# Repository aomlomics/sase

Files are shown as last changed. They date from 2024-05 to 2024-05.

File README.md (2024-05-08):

# sase

Subsurface Automated Sampler for eDNA (SASe)

Manuscript: Formel, N., Enochs, I. C., Sinigalliano, C., Anderson, S. R., & Thompson, L. R. (2021). Subsurface automated samplers for eDNA (SASe) for biological monitoring and research. HardwareX, 10, e00239. https://doi.org/10.1016/j.ohx.2021.e00239

Original code location (versions 1, 2, 3): https://data.mendeley.com/datasets/y3dgh36zt9/3

Files included (version 4):

File/folder name | File type | Open source license
-----------------|-----------|--------------------
SASeV4c.ino | Arduino code | CC BY 4.0
SASeBoard15 | Gerber Files | CC BY 4.0
SASe3DPrintFiles | 3Dprint Files | CC BY 4.0
SASeVectorFiles | Vector Files  | CC BY 4.0
BillofMaterials.docx | MS Word Doc | CC BY 4.0
BuildInstructions.pdf | PDF | CC BY 4.0
OperationInstructions.pdf | PDF | CC BY 4.0

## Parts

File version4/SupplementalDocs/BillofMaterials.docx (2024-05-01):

4. Bill of materials

Designator | Component | Number | Cost per unit (USD) | Total cost (USD) | Source of Materials | Material type
Fixed End Cap | Custom | 1 | $11.98* | $11.98 | 3D Printed on Form2 | Standard Black Resin
Flanged End Cap | Custom | 1 | $12.62* | $12.62 | 3D Printed on Form2 | Standard Black Resin
Acrylic Window | Custom | 1 | $0.50 | $0.50 | Laser Cut on BossLaser | Non-specific
Acrylic Test Cap | Custom | 1 | $0.50 | $0.50 | Laser Cut on BossLaser | Non-specific
End cap O-Ring | AS568-236 S70 Duro O-Ring | 1 | $0.56 | $0.56 | OringStore | Silicone
Lid | Custom | 1 | $11.43* | $11.43 | 3D Printed on Form2 | Standard Black Resin
Threaded inserts | Heat-sink threaded inserts (#4-40) | 4 | $0.19 | $0.77 | McMaster | Brass
Lid bolts | #6-32 x 1” Phillips Pan Head Machine Screws | 4 | $0.05 | $0.20 | AlbanyCountyFasteners | Stainless Steel
Lid nuts | #6-32 Nylon Insert Hex Lock Nuts | 4 | $0.04 | $0.16 | AlbanyCountyFasteners | Stainless Steel
PVC Pipe | 3” ID Schedule 40 PVC pipe, 4.25” long | 1 | $0.55 | $0.55 | HomeDepot | Non-specific
Motor Sleeve Left | Custom | 1 | $1.24* | $1.24 | 3D Printed on Form2 | Standard Black Resin
Motor Sleeve Right | Custom | 1 | $1.24* | $1.24 | 3D Printed on Form2 | Standard Black Resin
Motor Sleeve Screws | #4-40 x1/2” Phillips Pan Head Machine Screws | 8 | $0.03 | $0.24 | AlbanyCountyFasteners | Stainless Steel
Pumps | Peristaltic pumps-100 series 4mm Shaft; No Motor, 4 Rollers, 3mm Tubing Dia., Silicone Tubing | 2 | $9.92 | $19.84 | Williamson | Other
Pump Screws | #4-40 x 1” Phillips Pan Head Machine Screws | 4 | $0.05 | $0.20 | AlbanyCountyFasteners | Stainless Steel
Preservative Motor | 99:1 Metal Gearmotor 25Dx69L mm LP 12V with 48 CPR Encoder | 1 | $34.95 | $34.95 | Pololu | Other
Sample Motor | 34:1 Metal Gearmotor 25Dx69L mm LP 12V with 48 CPR Encoder | 1 | $34.95 | $34.95 | Pololu | Other
Motor shaft X-Rings | AS568-007 Buna-N 70 Durometer X-Rings | 2 | $0.07 | $0.14 | OringStore | Nitrile
Preservative Syringe | 10mL Luer Lock Dispensing Syringe | 1 | $0.82 | $0.82 | Grainger | Other
Filter | Sterivex™ filter 0.22um, luer lock (SVGVL10RC) | 1 | $10.79 | $10.79 | MilleporeSigma | Other
1/16” Tubing | 1/16” ID x 3/16” OD x 1/16” Wall Tubing, 2.75” long | 1 | $0.19 | $0.19 | USPlastics | Other
1/8 " Tubing | 1/8" ID x 1/4" OD x 1/16" Wall Tubing” 3" long | 1 | $0.23 | $0.23 | USPlastics | Other
Barbed Reducer | Straight Connector, 1/8" to 1/16" Barbed Reducer | 1 | $0.53 | $0.53 | Qosina | Other
Barbed Elbow | 1/8" Barb Elbow Connector | 1 | $0.50 | $0.50 | Qosina | Other
Barbed Tee | 1/8" Barb T Connector | 1 | $0.50 | $0.50 | Qosina | Other
Check Valve | Male-Female Luer Lock Check Valve, 2.9psi CP | 2 | $1.50 | $3.00 | Qosina | Other
Filter Barb | Male Luer Lock to 1/8" Barb Connector | 1 | $0.26 | $0.26 | Qosina | Other
Syringe Barb | Female Luer Lock to 1/16" Barb Connector | 1 | $0.21 | $0.21 | Qosina | Other
Straight connector | Straight Connector, 1/8" Barb | 1 | $0.00 | $0.00 | Williamson | Other
1/8" Clamp | Securing Clamp for 1/8" tubing | 8 | $0.25 | $1.97 | Qosina | Other
Sample Cartridge Cover | Custom | 1 | $6.51* | $6.51 | 3D Printed on Form2 | Standard Black Resin
Sample Cartridge | Custom | 1 | $7.11* | $7.11 | 3D Printed on Form2 | Standard Black Resin
Sample Cartridge Bolt | #6-32 x 1.25" Phillips Pan Head Machine Screws | 1 | $0.06 | $0.06 | AlbanyCountyFasteners | Stainless Steel
Sample Cartridge Wingnut | #6-32 Wingnut | 1 | $0.21 | $0.21 | AlbanyCountyFasteners | Stainless Steel
Housing Magnets | 1/8" Diameter x 1/16" Thick Magnet (D063CN52) | 8 | $0.56 | $4.48 | AmazingMagnets | Other
Circuit Housing | Custom | 1 | $4.26* | $4.26 | 3D Printed on Form2 | Standard Black Resin
Circuit Housing Faceplate | Custom | 1 | $4.53* | $4.53 | 3D Printed on Form2 | Standard Black Resin
Armature screws | #6-32 x 1.25" Flat Head Machine Screws | 2 | $0.05 | $0.10 | AlbanyCountyFasteners | Stainless Steel
Circuit Housing Screws | #4-40 3/4" Phillips Pan Head Machine Screws | 2 | $0.04 | $0.08 | AlbanyCountyFasteners | Stainless Steel
Circuit Board/Battery Cover Screw | #4-40 1/4" Phillips Pan Head Machine Screws | 3 | $0.03 | $0.09 | AlbanyCountyFasteners | Stainless Steel
IR Receiver | TSOP38238, 38.0kHz, 45m | 1 | $1.12 | $1.12 | Jameco | Other
OLED | 0.96 Inch Blue Yellow I2C OLED Display | 1 | $3.38 | $3.38 | AliExpress | Other
Reed Switch | 59050-010 | 1 | $1.18 | $1.18 | Digi-Key | Other
Microcontroller | Teensy 3.5 | 1 | $24.25 | $24.25 | PJRC | Other
microSD Card | 1gb microSD card, Class 4 | 1 | $4.95 | $4.95 | Sparkfun | Other
Coin Cell Holder | CR2032 Coin Cell Battery Holder | 1 | $0.07 | $0.07 | AliExpress | Other
Coin Cell | CR2032 Battery | 1 | $0.95 | $0.95 | Adafruit | Other
MOSFET | Power N-Channel MOSFET (IRLB8721) | 2 | $0.79 | $1.58 | Jameco | Other
Diode | 1N4004-TP Diode | 2 | $0.12 | $0.24 | Digi-Key | Other
1K Resistor | Resistor 1K 1/4W 1% AXIAL | 2 | $0.10 | $0.20 | Digi-Key | Other
390K Resistor | Resistor 390K 1/4W 1% AXIAL | 1 | $0.10 | $0.10 | Digi-Key | Other
100K Resistor | Resistor 100K 1/4W 1% AXIAL | 1 | $0.10 | $0.10 | Digi-Key | Other
3.3K Resistor | Resistor 3.3K 1/4W 5% AXIAL | 1 | $0.10 | $0.10 | Digi-Key | Other
Red Wire | 26 AWG Red Wire” 4" long | 1 | $0.05 | $0.05 | AllElectronics | Other
Battery Molex Connector | Molex 3 Position Connector Housing, 0022013037 | 1 | $0.19 | $0.19 | Digi-Key | Other
3-Pin Molex Connector | Molex 3 Position Connector Header, 0022232031 | 1 | $0.24 | $0.24 | Digi-Key | Other
Motor Molex Connector | Molex 6 Position Connector Housing, 0022013067 | 2 | $0.29 | $0.58 | Digi-Key | Other
6-Pin Molex Connector | Molex 6 Position Connector Header, 0022232061 | 2 | $0.43 | $0.86 | Digi-Key | Other
Crimp | Molex Connector 22-30AWG Crimp, 0008650816 | 15 | $0.29 | $4.35 | Digi-Key | Other
Circuit Board | Custom | 1 | $0.49 | $0.49 | SeeedStudio | FR-4
Battery Housing | Custom | 1 | $10.13* | $10.13 | 3D Printed on Form2 | Standard Black Resin
Battery Housing Cover | Custom | 1 | $1.66* | $1.66 | 3D Printed on Form2 | Standard Black Resin
Battery Cover Screws | #4-40 1/4" Phillips Pan Head Machine Screws | 2 | $0.03 | $0.06 | AlbanyCountyFasteners | Stainless Steel
Armature to Lid Screws | #6-32 1/4" Phillips Pan Head Machine Screws | 2 | $0.04 | $0.08 | AlbanyCountyFasteners | Stainless Steel
1/4” Heatshrink | 1/4" Heatshrink” 1" long | 1 | $0.02 | $0.02 | AllElectronics | Other
1/16" Heatshrink | 1/16" Heatshrink” 1" long | 1 | $0.01 | $0.01 | AllElectronics | Other
Header Pins | 24 Position Header Pin 2.54mm, 0022284240 | 1 | $0.82 | $0.82 | Digi-Key | Other
Batteries | AA Rechargeable NiMH | 8 | $4.17 | $33.35 | BatteryJunction | Other
IR Remote | Mini Remote Control, 21 Buttons, 38KHz NEC code output, 940nm IR LED | 1 | $4.95 | $4.95 | Adafruit | Other
Magnet | Any Standard Magnet | 1 | $0.75 | $0.75 | AmazingMagnets | Other
Preservative** | DNAGard (62001-046) 100mL | 1 | $240 | $240 | Biomatrica | Other
Solder | 24 AWG Lead-Free Wire Solder | 1 | $21.97 | $21.97 | Digi-Key | Other
Epoxy | E-90FL 2-Part Epoxy | 1 | $14.38 | $14.38 | Zoro | Other
Lubricant | Multi-Purpose Synthetic Grease | 1 | $4.69 | $4.69 | Walmart | Other

* The cost of 3D printed items was based on the cost of Formlabs standard black resin and the volume required

**The preservative identified here, DNAGard is no longer in production. However other preservatives can be substituted in the SASe that similarly allow ambient condition preservation of DNA such as Zymo Research DNA/RNA Shield (R1100-250)

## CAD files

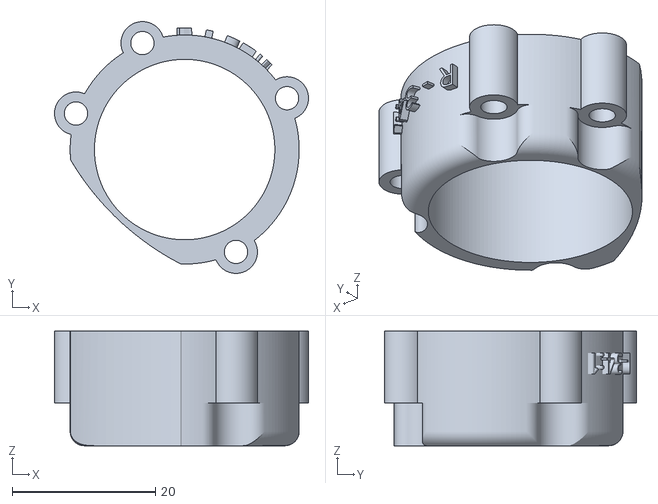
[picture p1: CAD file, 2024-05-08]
version4/DesignFiles/SASe3DPrintFiles/motorSleeveRight.stl
35.5 x 35.2 x 16.0

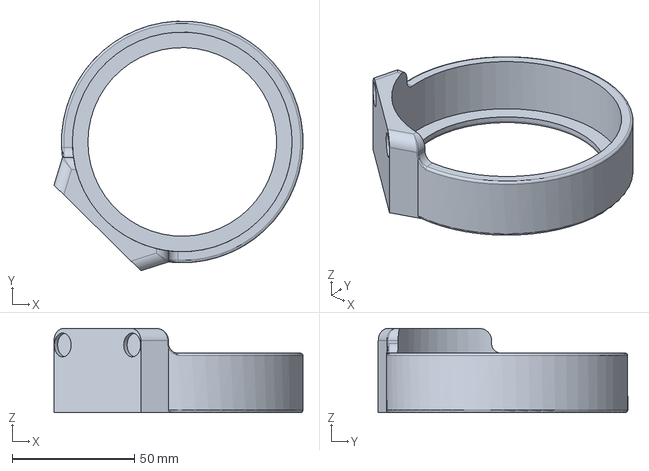
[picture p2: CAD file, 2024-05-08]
version4/DesignFiles/SASeStepFiles/SASe_fixedCap.step
102.0 x 102.2 x 34.5 mm

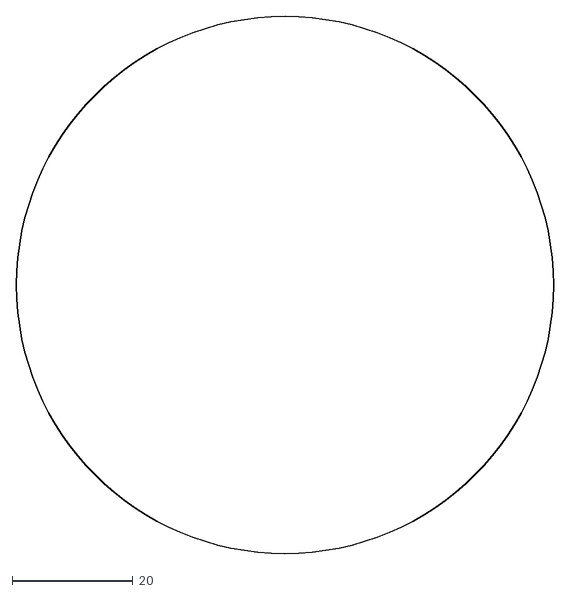
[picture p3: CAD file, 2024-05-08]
version4/DesignFiles/SASeVectorFiles/acrylicWindow.dxf
88.9 x 88.9

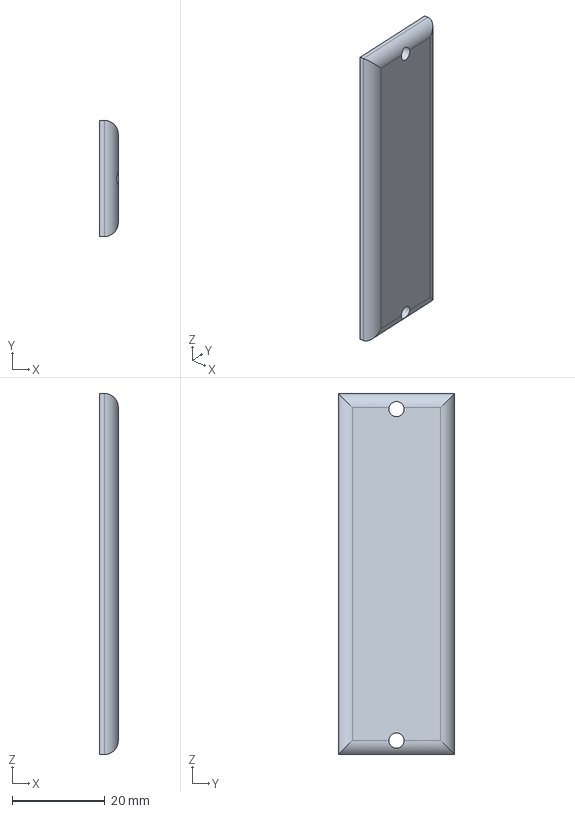
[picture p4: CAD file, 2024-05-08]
version4/DesignFiles/SASeStepFiles/SASe_battCover.step
4.00 x 25.0 x 77.7 mm

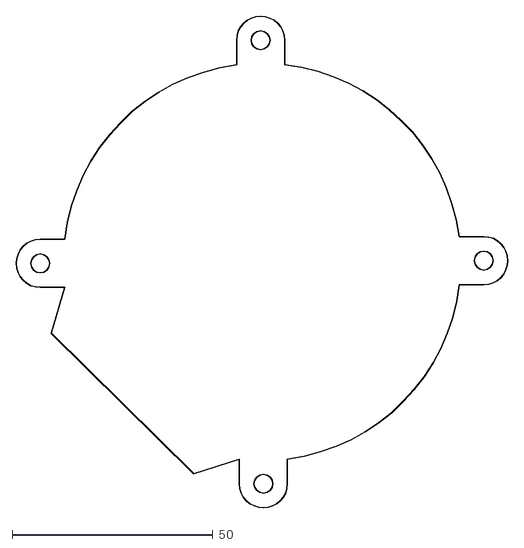
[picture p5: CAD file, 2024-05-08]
version4/DesignFiles/SASeVectorFiles/acrylicTestCap.dxf
122.5 x 122.5

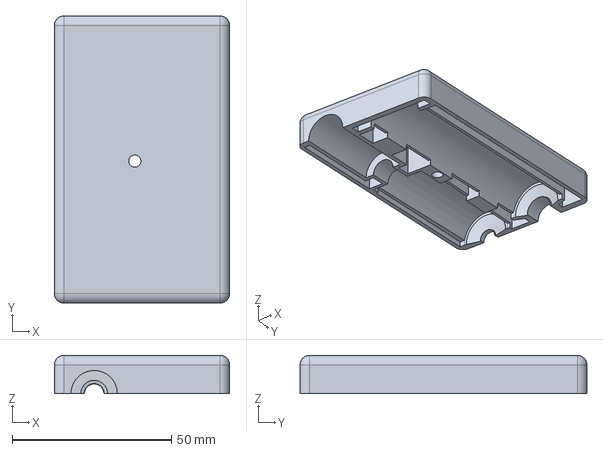
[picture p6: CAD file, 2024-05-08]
version4/DesignFiles/SASeStepFiles/SASe_topCover.step
55.0 x 90.0 x 12.0 mm

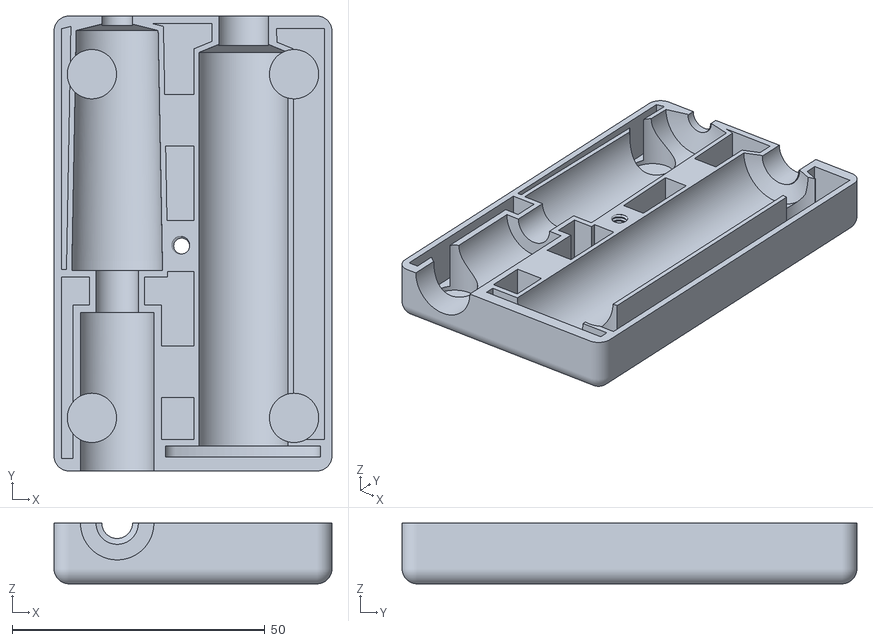
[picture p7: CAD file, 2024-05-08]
version4/DesignFiles/SASe3DPrintFiles/sampleCartridge.stl
55.0 x 90.0 x 12.0

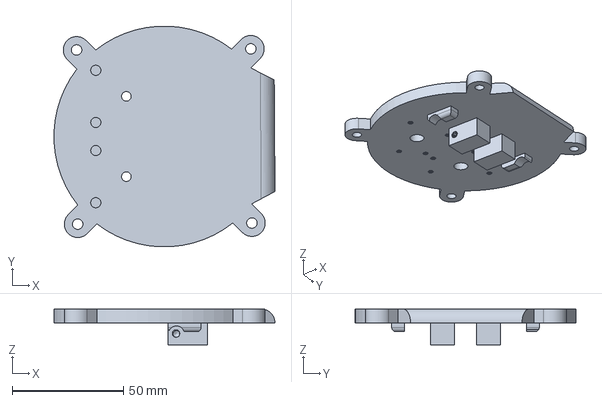
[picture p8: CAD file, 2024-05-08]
version4/DesignFiles/SASeStepFiles/SASe_motorMount.step
99.1 x 98.9 x 16.1 mm

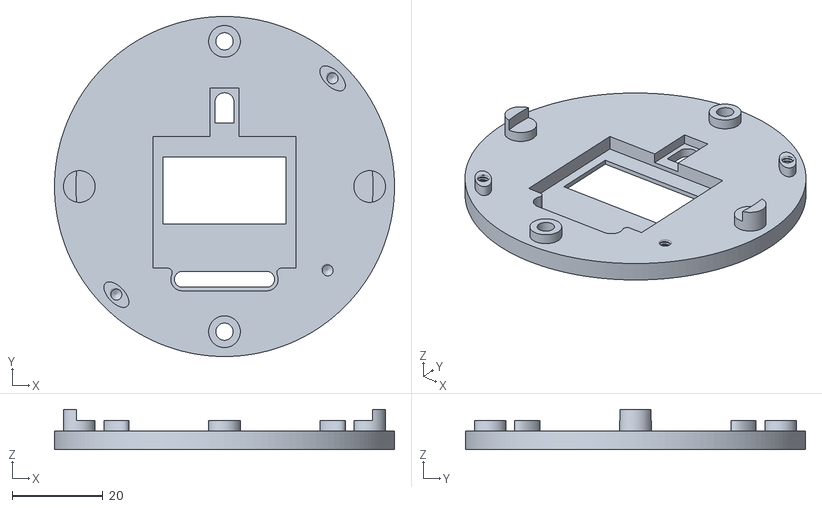
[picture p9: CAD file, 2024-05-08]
version4/DesignFiles/SASe3DPrintFiles/saseCHFacePlate.stl
74.9 x 74.9 x 8.93

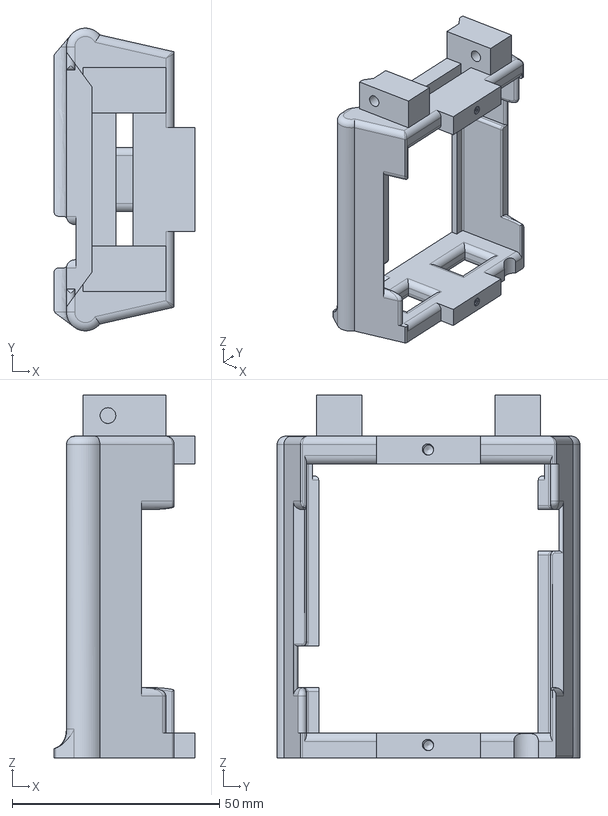
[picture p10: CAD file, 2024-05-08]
version4/DesignFiles/SASeStepFiles/SASe_battHolder.step
34.0 x 73.1 x 87.7 mm

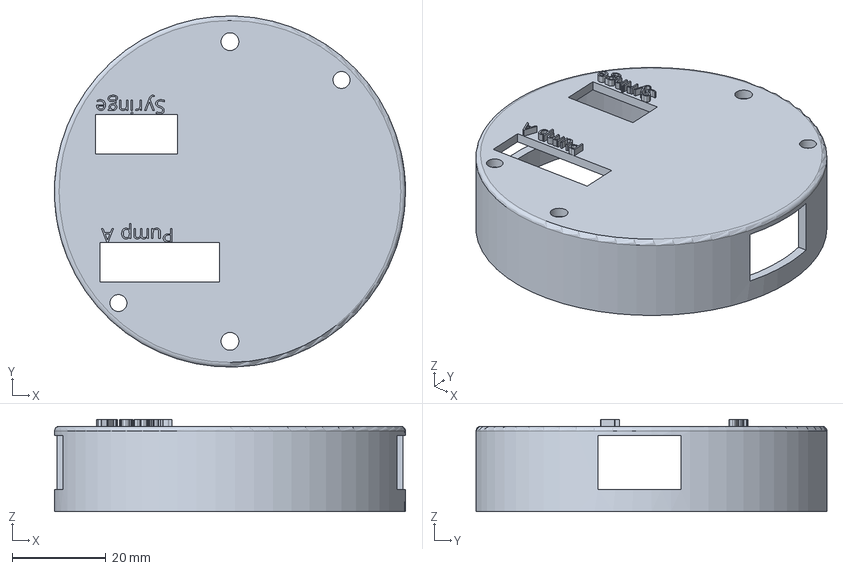
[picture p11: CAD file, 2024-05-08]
version4/DesignFiles/SASeStepFiles/SASe_circuitHousing.step
75.0 x 75.0 x 19.7 mm

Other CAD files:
version4/DesignFiles/SASe3DPrintFiles/saseFixedEndCap.stl
version4/DesignFiles/SASe3DPrintFiles/motorSleeveLeft.stl
version4/DesignFiles/SASe3DPrintFiles/sampleCartridgeCover.stl
version4/DesignFiles/SASeStepFiles/SASe_bottomCover.step
version4/DesignFiles/SASeStepFiles/SASe_facePlate.step
version4/DesignFiles/SASeStepFiles/SASe_motorSleeve2.step
version4/DesignFiles/SASeStepFiles/SASe_motorSleeve1.step
version4/DesignFiles/SASe3DPrintFiles/saseBattCover.stl
version4/DesignFiles/SASe3DPrintFiles/saseCircuitHousing.stl
version4/DesignFiles/SASeStepFiles/SASe_3inch_endcap.step

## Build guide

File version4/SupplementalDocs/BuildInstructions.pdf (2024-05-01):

### 5. Build instructions

All the 3D printed components in the design were made with SLA 3D printers. The SLA style

ensures the parts are waterproof, however, that need only applies to the three external parts

(fixed end cap, flanged end cap, and lid). The internal components could be made with a

different 3D printing style or other production method provided form was consistent with the

design. For 3D printing the default settings of the printer were used with a print resolution of

0.1mm and supports with rafting.

### 5.1. Housing construction

To prepare the components of the housing, sand the joining faces of the 3D printed end caps,

acrylic window, and the PVC pipe (Fig. 1) to improve adhesive bonding. Throughout the

construction process be sure to clean and dry areas prior to epoxying and remove excess epoxy to

avoid issues with fit and function. Apply a heavy bead of 2-part epoxy along the inside edge of

the flanged end cap (Fig. 2) and along the outside edge of one end of the PVC pipe. Push the

flanged end cap onto the PVC and give it a quarter twist to ensure even spread of the epoxy.

Place the joined parts with the end cap down and weight the PVC to improve stability during

curing of the epoxy, which should take 18-24 hours.

Apply a heavy bead of 2-part epoxy along the inside edge of the fixed end cap and press the

acrylic window into the end cap. Twist the acrylic window as needed to ensure even spread of

the epoxy and set the end cap with the acrylic facing up. Weight the acrylic to improve stability

during curing of the epoxy.

Once both parts are fully cured, add a heavy bead of 2-part epoxy along the inside wall of the

fixed end cap and the outside uncapped edge of the PVC pipe. Insert the PVC into the fixed end

cap and give the PVC a quarter twist to ensure even spread of the epoxy. At this point make sure

the magnet holes on the end caps are lying on the same plane and lined up. Failure to line up

these two surfaces will prevent the sampling cartridge from securely attaching. Once the fixed

cap is in place and lined-up set the housing down and weight the top piece to improve stability

during curing of the epoxy.

Once the housing is fully cured, insert the #6-32 x 1” bolts into the flanged end cap threaded

holes. Apply a small amount of lubricant to the end cap O-ring and place in the O-ring groove of

the flanged end cap. Install the acrylic test cap using the #6-32 lock nuts. Tighten the nuts down

until the O-ring is visually compressed. Throughout the construction process, be cautious

tightening screws on 3D printed parts to avoid overtightening and damaging the printed

components. Submerge the housing in water and watch for air bubbles escaping, which would

indicate a leak, and look for signs of water entry through the acrylic window. Minor leaks may

be fixed by identifying the location and adding more epoxy. This water test is not required but is

useful to prevent the discovery of leaks after the motors and electronics are installed, especially

on the first build.

### 5.2. Motor installation

Match the 34:1 motor with the 3D printed right motor sleeve, and the 99:1 motor with the left

sleeve and sand the contact faces of the top of the motors and the insides of the sleeves. Put a

heavy bead of 2-part epoxy around the top of the motor body and slide the motor sleeve onto the motor, twisting it around to improve the even spread of epoxy. Place the motor shaft-down with

the face of the motor and the face of the motor sleeve flush during curing. A board with holes for

the motor shaft can serve as a helpful jig for this step (Fig. 3). Failure to keep the motor and

sleeve face flush can impact the stability of the motor mount on the SASe lid.

To install the threaded #4-40 fittings into the SASe lid, first partially screw the fitting onto a #4-

40 screw. Apply a coat of 2-part epoxy to the outside of the fitting and then push the fitting into

position until the top is flush with the top of the lid (Fig. 3). Leave the fitting in place, carefully

remove the screw, and avoid pushing epoxy inside the fitting while the epoxy cures.

Once the motor sleeves are cured onto the motor, clip the length of the motor wires to 3.5 inches.

Run the wires for each motor through a 0.5-inch long piece of 1/4-inch heat shrink tubing. Install

a crimp onto the end of each wire and insert the crimped wires for each motor into a motor

Molex connector matching the original order (Fig. 4). Arrange the heat shrink tubing about

midway between the motor and the connector and apply heat to shrink for better wire

organization.

Apply a small amount of lubricant to the motor shaft X-rings and install them into the X-ring

seats on the inside of the SASe lid, using the shaft of the motor to push them into place. Once X-

rings are installed, push the shaft of the motors through the shaft holes in the lid. The 34:1 motor

used for sample collection and the 99:1 motor used for pumping preservative are positioned as

shown in Figure 5. Secure the motors in place with the #4-40 x ½ inch screws through the motor

sleeves. The screws will fit flush with the motor sleeves and should not be more than “finger

tight”.

Once the threaded fittings have cured in the lid, install the two peristaltic pumps onto the motor

shafts, oriented so the pump mounting holes line up with the fittings. Secure the pumps in place

using the #4-40 x 1-inch screws. Install the 1/8-inch barbed connector into the left tube of the

sample pump head (Fig. 6). Cut the 1/8-inch tubing into a 2.25-inch long piece and a 3/4-inch

long piece. Install the 1/8-inch barb tee connector on one end of the 2.25-inch long section and

the 1/8-inch male luer lock fitting on the other end. Attach the 3/4-inch section of tubing to the

free end of the tee. On the other end of the tubing attach the 1/8-inch elbow connector. Slide a

1/8-inch tube clamp onto the inside tube of each pump and then install the fitting/tubing combo

into the two pump heads as pictured in Figure 6. Once inserted, tighten clamps to secure the

fittings. Insert the 1/8-inch to 1/16-inch reducer fitting into one end of the 2.75-inch long 1/16-

inch tubing. On the free end of the 1/16-inch tubing, insert the 1/16-inch barb to female luer lock

fitting. Insert the 1/8-inch barb into the free tube of the preservative pump to complete the SASe

plumbing.

At this point, the housing can be water-tested again to ensure the X-rings were installed properly.

Install the lid with mounted motors and pumps and secure with the #6-32 lock nuts. Submerge

the housing in freshwater and ensure there are no leaks.

### 5.3. Power source construction

The battery pack holds eight AA batteries and has ground and 12-volt wire connections. To add a

6-volt power source, install the 4-inch red wire into the battery pack midway between the 12-volt

wire and the ground wire (Fig. 7). To install the wire, strip 1/8-inch of the insulation off one end

of the wire and 1/4-inch of the insulation off the other end. Put the 1/4-inch side of the wire

through the negative terminal indicated in Figure 7 and wrap the uninsulated wire around the

terminal to make a more stable connection, then solder the wire in place. Clip the original wires

to match the length of the new 6V wire, using the connection of the 6V wire as the starting point

for measurement, and strip off an 1/8-inch of insulation from the ends. Put a 1-inch long piece of

1/16-inch heat shrink around the wires to keep them together and install a crimp on the end of

each of the three wires. Install the wires into the battery Molex connector (Fig. 7).

Attach the 3D-printed battery housing to the lid using the two #6-32 x 3/4-inch long armature to

lid screws. With the battery pack updated, install eight AA batteries and insert the battery pack

into the 3D-printed battery housing. Secure the battery pack in place with the 3D-printed cover

and the two #4-40 x 1/4-inch long screws.

### 5.4. Circuit board construction

The circuit board can be milled in-house, but the quality and cost of ordering printed circuit

boards (PCB) make that the better option. This project had circuit boards milled by Seeed Studio

(seeedstudio.com/fusion.html) using the circuit board design files (SASeBoard15.zip) and the

following parameters:

PCB Dimension: 64.2mm*64.2mm

Impedance Control: No

Surface Finish: HASL

Min Solder Mask Dam: 0.4mm↑

Copper Weight: 1oz.

Half-cut / Castellated Holes: No

Min Hole Size: 0.3mm

PCB Color: Blue

Material: FR4 TG130

Layer: 2

Blind Vias: No

PCB Thickness: 1.6mm

Min Tracking / Spacing: 6/6mil

Plated Half-holes / Castellated Holes: No

Installation of the circuit board components is described here in order of installation. Solder the

headers, resistor, and diodes in place on the PCB (Fig. 8). The direction of the resistors is not

important but take care to orient the diodes as pictured on Figure 8 to ensure proper current flow.

Clip the excess pins from the bottom of the board. Install the 3-pin and two 6-pin Molex

connectors and solder the pins on the bottom of the board. Install the MOSFETs with enough

clearance to be bent at an angle above, but not touching, the diodes. Solder the MOSFETs in

place and clip the excess pins from the bottom of the board. Solder the 4-pin header onto the

OLED, and then flip the PCB over and install and solder the OLED in place on the bottom of the

board (Fig. 9). Bend the IR receiver pins at a right angle to the receiver and install and solder the

receiver with about 2 mm of space between the back of the receiver and the board. Install the reed switch in place and solder the pins. Clip any excess pins on the top of the board. Install the

RTC coin cell battery holder into the top of the board (Fig. 10). To solder the battery holder pins

the IR receiver on the bottom of the board needs to be bent gently upwards. Once the pins are

soldered and clipped, gently bend the receiver back into a horizontal position. Lastly, install the

Teensy on the headers and solder in place.

### 5.5. Preparation of the microSD card and software programming

Using a text editor program, create the two text files for recording sample logs (dataLog.TXT)

and storing settings and sample parameters (sampleParam.TXT). The dataLog file is a blank file

for logging sample times and requires no text. The sampleParam file requires a line of text with

nine integers.

Example: 1,1000,10,-1000,11,30,18,11,19

Key: Sample Mode (0 = Daily, 1= Once), Sample Volume (mL), Calibration Volume (mL),

Calibration Count, Sample Time (Hr), Sample Time (Min), Sample Day, Sample Month, Sample

Year

Input an appropriate line of text for the sampleParam file, save both text files on the microSD

card, and insert the card into the Teensy.

To upload the operating code to the SASe requires the Arduino software (IDE) and the

Teensyduino add-on. Once installed, place the SASe code (SASeV3c.ino) in a folder labeled

identically (i.e., SASeV3c) within the Arduino library folder. Run the Arduino program and use

the Library Manager to search for and install the most recent versions of:

- Adafruit GFX Library by Adafruit

- Adafruit SSD1306 by Adafruit

Also, because more recent versions have not been made compatible at this time, install version

1.1.4 of:

- SdFat by Bill Greiman

To set the OLED display resolution navigate to the Adafruit_SSD1306 folder (…\Arduino\

libraries\). Open the Adafruit_SSD1306.h file with a text editor and scroll down to the following

line:

// | #define SSD1306_128_64
| #define SSD1306_128_32
// | #define SSD1306_96_16

The default setting is the 128 x 32 bit screen resolution but the SASe OLED resolution is 128 x

64 bit. To fix this, uncomment the 128 x 64 bit screen resolution by deleting the two forward

slashes in front of SSD1306_128_64 and add two forward slashes in front of SSD1306_128_32:

#define SSD1306_128_64

// | #define SSD1306_128_32
// | #define SSD1306_96_16

Save and close the text file. To maximize sleep time for the Teensy and the SASe, the low

current draw Snooze library needs to be edited. Navigate to the Snooze src folder

(…\Arduino\hardware\teensy\avr\libraries\Snooze\) and use a text editor to edit and save these two files: SnoozeAlarm.h and SnoozeAlarm.cpp. In SnoozeAlarm.h find the line near the bottom

of the document that reads:

void setRtcTimer( uint8_t hours, uint8_t minutes, uint8_t seconds );

Change that line to:

void setRtcTimer( uint32_t hours, uint32_t minutes, uint32_t seconds );

In SnoozeAlarm.cpp, find the line near the top of the document that reads:

void SnoozeAlarm::setRtcTimer( uint8_t hours, uint8_t minutes, uint8_t seconds ) {

Change that line to:

void SnoozeAlarm::setRtcTimer( uint32_t hours, uint32_t minutes, uint32_t seconds ) {

Save and close both text files. The SASe code is ready to be uploaded onto the Teensy

microcontroller. Use the Arduino program to open the SASe code. Under the Tools menu select

“Board:” and choose Teensy 3.5. Connect the Teensy microcontroller to the computer with a

micro USB to USB cord. Under the Tools menu select “Port:” and choose the serial port

connected to the Teensy. Select the Upload arrow in the top left corner to verify and compile the

code onto the Teensy. Verify the upload worked by looking at the OLED on the circuit board. If

it worked, the screen will display the Status Menu. Once the code is uploaded and the OLED is

displaying properly, disconnect the Teensy and install the circuit board into the 3D printed

faceplate using one #4-40 x 1/4-inch screw (Fig. 10). Install the 3D printed circuit housing on the

faceplate, being sure to line up the Molex connectors with the openings in the housing (Fig.

11A). Attach the circuit housing to the faceplate using two #4-40 x 3/4-inch screws. Attach the

completed circuit housing to the armature using two #6-32 x 1.25-inch screws (Fig. 11B).

### 5.6. Sampling cartridge construction

To install the magnets for the sampling cartridge and end caps it is important to keep track of the

polarity of the magnets so that they are all installed in the same direction. Put a dot of two-part

epoxy into each of the magnet spaces on the bottom of the sampling cartridge and then press the

magnets into place until fully seated (Fig. 12). The magnets in the end caps of the SASe must

also be installed with the polarity in the same direction as the sampling cartridge magnets. Place

a dot of two-part epoxy in the magnet spaces on each of the end caps and press the magnets into

position. Allow all epoxied magnets to cure before testing. Once cured, attach the cover of the

sample cartridge using the #6-32 x 1.25-inch bolt and the #6-32 wingnut, then attach the

sampling cartridge to the SASe housing via the magnets.

### 5.7. Final preparation

With all components now complete, connect the two pump motors and the power connection to

the circuit board. The circuit housing is labeled to identify where each motor attaches. Connect

the preservative motor to the 6-pin Molex connector labeled “Syringe”, connect the sample

motor to the 6-pin Molex connector labeled “Pump A”, and connect the battery to the 3-pin

Molex connector inside of the sample motor connection (Fig. 13). Route the wires so they are not

touching the motor rotary encoders to avoid wear on the wires when the motors are running. If

properly assembled, the SASe OLED will turn on and display the Status Menu. Slide the internal

components of the SASe into the waterproof housing and secure the lid with the four lock nuts.

Figures:

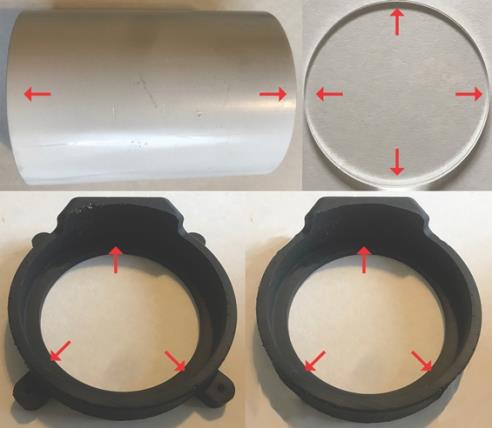
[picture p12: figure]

Figure 1: Red arrows indicate the surfaces to sand and clean in preparation for epoxying.

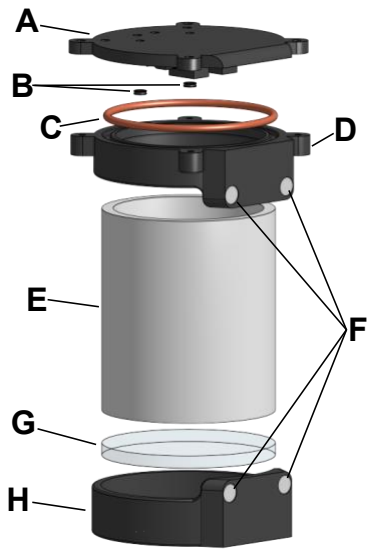
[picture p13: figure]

Figure 2: The SASe housing is made up of a 3D-printed lid (A), two X-rings for the motor shafts

(B), O-ring for the lid seat (C), 3D-printed flanged end cap (D), 3” PVC body (E), four sample

cartridge connection magnets (F), ¼” acrylic window (G), and a 3D-printed fixed end cap (H).

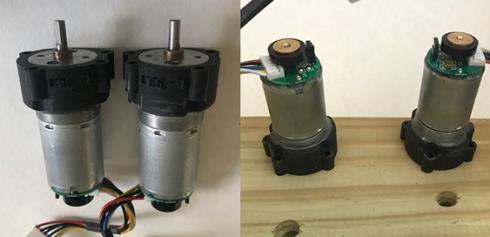
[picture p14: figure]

Figure 3: The motor sleeves and the face of the motor need to be flush. Using a jig can help hold

that position while the epoxy is curing.

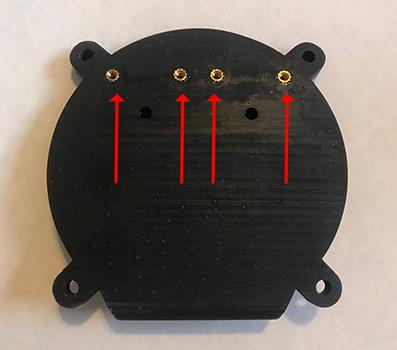
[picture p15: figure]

Figure 4: Threaded fittings are installed on the outside face of the 3D printed lid.

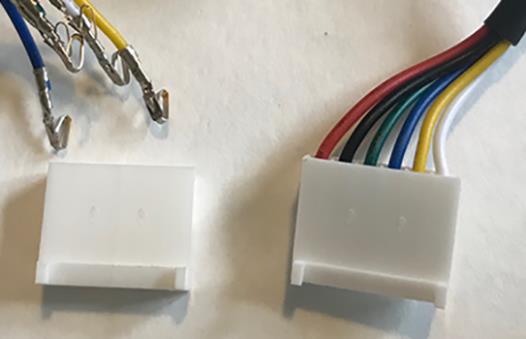
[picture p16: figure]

Figure 5: The crimped wires are inserted in the motor connectors in the order shown on the right.

Wire ID: Red (Power), Black (Power), Green (Ground), Blue (VCC), Yellow (Encoder A

output), White (Encoder B output).

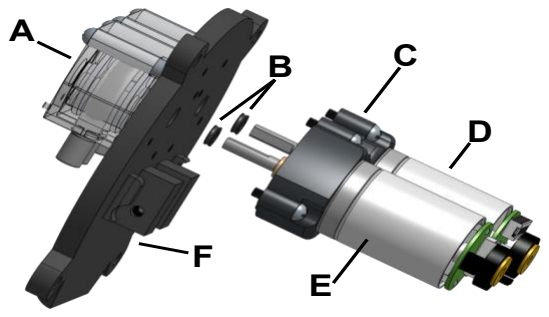
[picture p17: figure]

Figure 6: The two peristaltic pumps (A) are mounted to the outside of the 3D-printed lid (F). The

34:1 (D) and the 99:1 (E) DC motors are epoxied to 3D-printed motor sleeves (C) mounted on

the inside of the lid. The motor shafts insert into the peristaltic pumps through the lid and an X-

ring on the shaft of each of the motors (B) keeps the shaft-lid interface watertight.

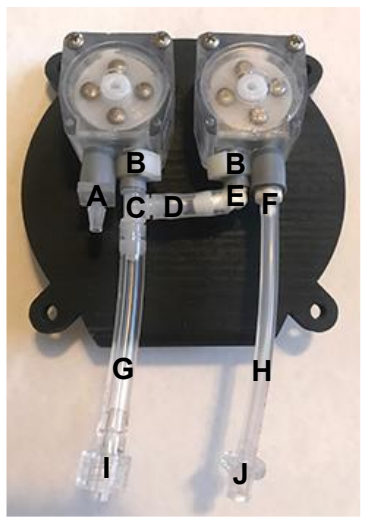
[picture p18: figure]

Figure 7: The pump heads are secured on the outside of the SASe lid, and the plumbing

components for transporting sample water and preservative are installed as pictured and include

the 1/8-inch barbed connector (A), 1/8-inch tube clamps (B), 1/8-inch barb tee connector (C),

0.75-inch long 1/8 ” tubing (D), 1/8-inch elbow connector (E), 1/8-inch to 1/16-inch reducer

fitting (F), 2.25-inch long 1/8-inch tubing (G), 2.75-inch long 1/16-inch tubing (H), 1/8-inch

male luer lock (I), 1/16-inch barb to female luer lock fitting (J).

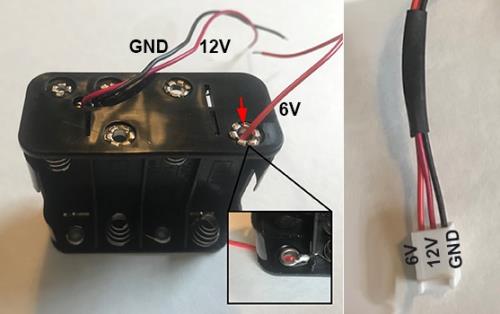
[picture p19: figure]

Figure 8: Solder a 6V wire to the OEM battery pack at the terminal indicated by the red arrow.

The inset shows the wire looped around the inside of the terminal to add stability to the

connection. Install the crimped wires into the Molex connector as pictured.

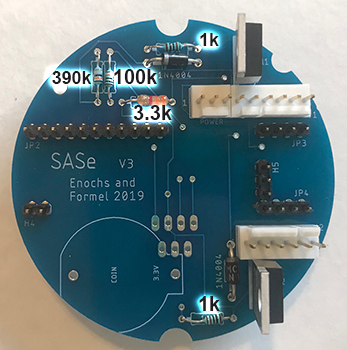
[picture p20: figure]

Figure 9: The headers, resistors, diodes, MOSFETs, and Molex connectors are installed as

pictured.

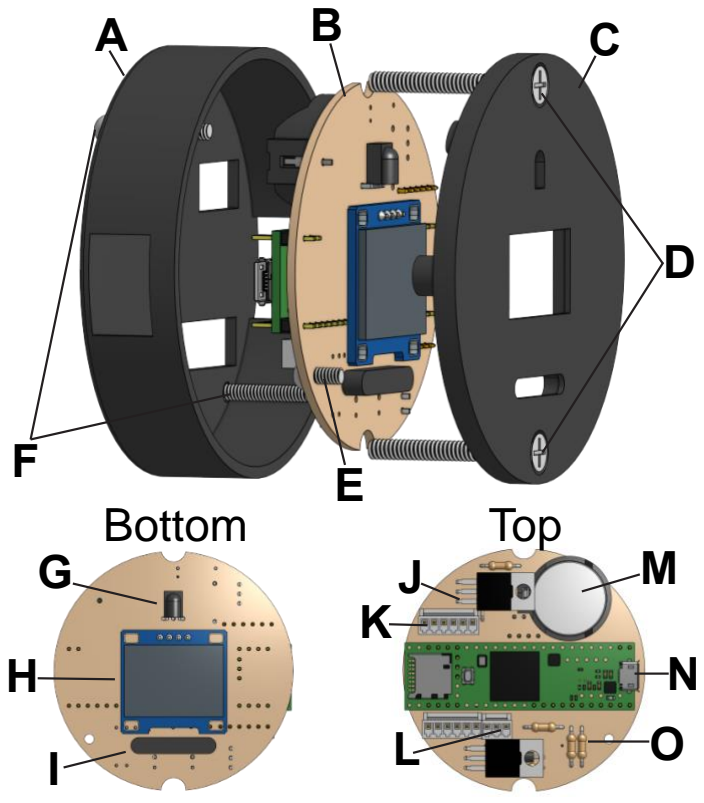
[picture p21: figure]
Bottom; Top

Figure 10: The 3D-printed circuit board housing (A) holds the SASe circuit board (B) and the UI

components are visible through the 3D-printed faceplate (C). The whole housing is mounted on

the main armature with two #6-32 bolts (D), while one #4-40 bolt (E) secures the circuit board to

the faceplate, and two #4-40 bolts (F) hold the housing together. The circuit board is labeled to

show the top and bottom and all PCB components are labeled as follows: IR receiver (G), OLED

(H), reed switch (I), N-channel MOSFET (J), Molex 6-pin connector (K), Molex 3 pin connector

(L), coin cell battery (M), Teensy 3.5 (N), resistors (O). Not visible are the two diodes below the

MOSFETs that control current flow for the motor circuits.

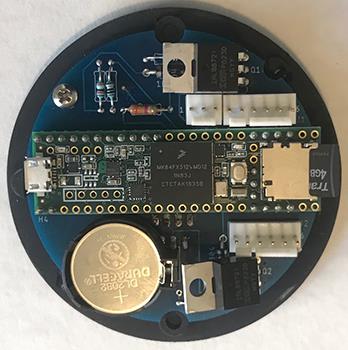
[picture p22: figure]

Figure 11: Install the coin cell holder and solder the pins on the bottom of the board then install

the Teensy microcontroller and solder the pins. The finished circuit board is installed onto the 3D

printed faceplate.

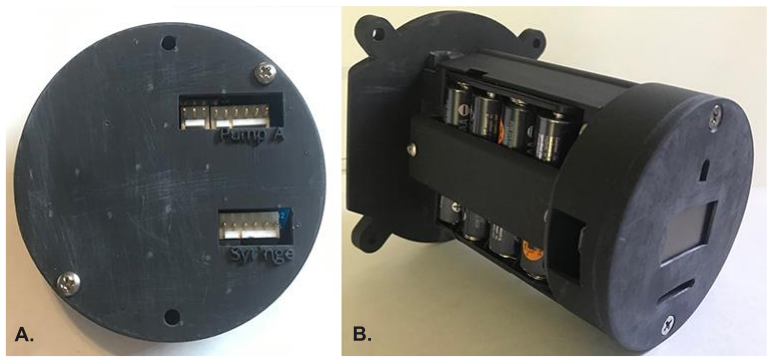
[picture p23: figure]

Figure 12: The 3D printed circuit housing (A) with openings for Molex connectors is attached to

the armature (B) to connect the internal components of the SASe.

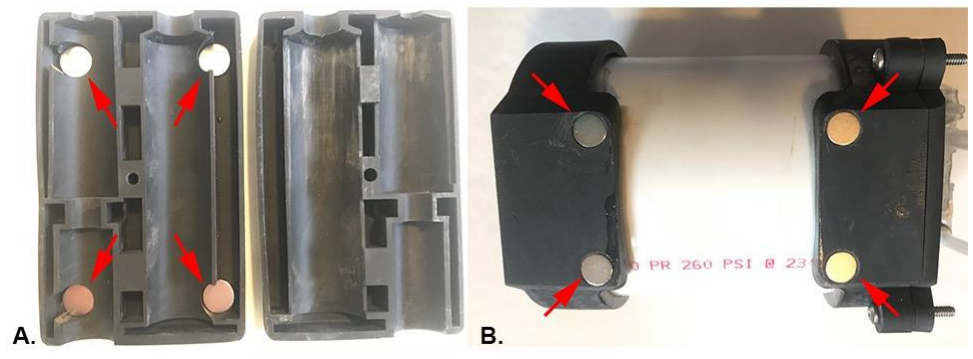
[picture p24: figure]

Figure 13: The sample cartridge (A) and the end caps (B) both require magnets installed as

indicated by the red arrows.

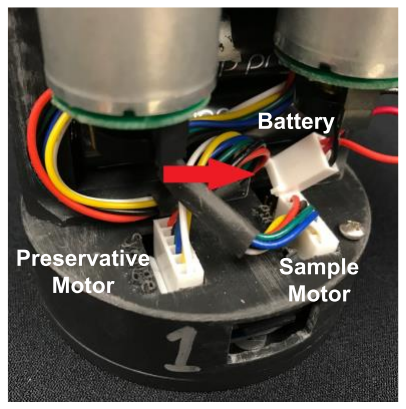
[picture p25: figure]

Figure 14: The connections for the SASe motors and battery are labeled, and the battery

connection location is indicated by the red arrow.

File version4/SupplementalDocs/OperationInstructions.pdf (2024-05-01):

### 6. Operation instructions

### 6.1. User interface

Once the batteries are attached to the SASe circuit board the OLED screen will turn on and

display the Status Menu (Fig. 1). To navigate through and within the SASe menu screens, use the

four cursor keys and the enter button of the IR remote, the left and right cursors will navigate

between menus from the top of the screen (Fig. 2). Settings are saved by selecting “ENTER

SET” and pressing enter.

### 6.2. Calibration

The peristaltic pumps have an advertised pump rate of 0.2mL per revolution, but there is

variability by pump head, so a calibration step uses the motor’s rotary encoder and user input to

measure the actual pump rate and improve accuracy of sampling volume. To run the calibration,

install a fresh Sterivex filter onto the filter luer lock connection, including the one-way check

valves on either end of the filter (Fig. 3). Connect a piece of 1/8-inch tubing to the inflow

connection of the sampling pump and put the other end of the tubing into a water cup. Direct the

outflow of the filter into a graduated cylinder. With the Status Menu on the screen press the left

cursor on the IR remote to navigate to the Prime Menu. Use the down cursor on the IR remote to

navigate the cursor to the row labeled “RUN WATER”, then hit enter on the remote. The

sampling pump will turn on and can be turned off by pressing enter on the remote again. The

tubing and filter should be fully primed with water before starting the calibration to ensure

accurate results. Position the outflow of the filter to flow into an empty graduated cylinder. Use

the left cursor to navigate to the Calib Menu. Select “RUN CAL” and press the enter key on the

IR remote. The sampling pump will turn on for 30 seconds. Measure the amount of water transferred to the graduated cylinder when the pump stops. Use the IR remote and the up and

down cursors to enter the volume of water collected on the “VOL:” line. Select ENTER SET and

press enter to save the calibration. The screen will display <SAVED> to show it was saved.

After calibration, the sampling pump has an accuracy of ±5% of the target volume (Fig. 4).

### 6.3. Set time

Once the calibration is set, the RTC on the microcontroller should be set. Navigate to the Time

menu. The first row is the time in HH:MM:SS and the second row is the date in DD/MM/YY.

Change the numbers using the up and down cursors to match up with the time and date. Select

and press enter on “ENTER SET” to synchronize the RTC with set time. The correct time will

now be displayed in the Status Menu.

### 6.4. Set sample mode, collection time, and date

The sampler can operate in two different modes: Once and Daily. Once mode will sample a set

volume at a single given time and date and then wait in sleep mode until woken up and

reprogrammed. Daily mode will sample a set volume at a given time every day starting on the

date selected. Navigate to the Settings Menu and select “Mode”; use the up and down cursor to

switch between “Once” and “Daily”. The next line allows the sample volume to be adjusted. The

up and down cursors can be used to increase or decrease the volume in increments of 10 mL with

an upper limit of 2000 mL. Once the mode and volume have been chosen, select “ENTER SET”

and press enter to save the settings.

Navigate to the Pump Menu. The first line (T) is the time setting for an alarm to go off and activate the sampling programming while the second line (D) is the date. Both options will

always be available, but the date will only be displayed on the Status Menu for Once Mode.

Daily mode uses the pump date to determine when daily sampling begins, but on the Status

Menu only the time of sampling will be displayed. Use the up and down cursors to adjust the

time (HH:MM) and date (DD/MM/YY) and then select “ENTER SET” and press enter to save

the pump alarm time. Navigate to the Status Menu to review the input settings and confirm the

current time.

### 6.5. Initiate sampling mode

After calibrating the sampler and inputting the settings the pump needs to be in a sleep mode to

save battery life and initiate sampling tasks. Navigate to the Initiate Menu. Select “Press Enter”

and press enter on the IR remote. The sampler will go into sleep mode. The time, date, and

battery voltage will be logged on the dataLog.txt file on the microSD card when sampling starts.

If the SASe is set to go off within 60 seconds of sleep mode being initiated “Wait...” will be

displayed on the screen until the sampling starts. When the sampling mode begins, the sampling

pump is activated and the screen will read “SAMPLING”. At this point the pump will run until

the programmed volume of water has been filtered and the program cannot be interrupted with

the reed switch. Once the sample has been taken, the sampling pump will turn off and the

preservative pump will turn on. The screen will read “SYRINGE” and the preservative pump

will run until five mL of preservative has been pumped into the filter housing. If the SASe is set

to Once mode it will return to sleep mode and stay that way until woken up with the reed switch

or until the batteries die. If it is in Daily mode it will add 24 hours to the sample time and date and start sleep mode again, until the sampler is woken up with the reed switch or until the

batteries die.

### 6.6. Interrupt sampling mode

While the SASe is in sleep mode, no changes can be made to the settings. To wake the sampler

up from sleep mode and allow changes to be made, the reed switch on the face of the sampler

must be activated. To activate the reed switch, press a magnet against the acrylic faceplate and

move it back and forth in front of the black reed switch (Fig. 2). After 2-3 seconds, the sampler

will come out of sleep mode and display “REED!” on the OLED before displaying the Status

Menu.

### 6.7. Deployment

Before deploying the SASe the O-ring should be lubricated, fully charged batteries installed, and

all securing screws and nuts carefully tightened to ensure a waterproof seal. Take care when

lubricating the O-ring to ensure it is clean of dirt, hair, or other debris that could break the

waterproof seal. Install a new Sterivex filter capped by check valves into the sampling cartridge

and fill the preservative syringe. Secure the cover of the sampling cartridge using the #6-32 bolt

and wingnut. Attach the filter connection and the syringe connection to the filter inflow check

valve and the syringe, respectively (Fig. 3). Attach the filter cartridge to the SASe housing via

the magnets.

To prevent an airlock in the tubing or compression of the filter air space when the SASe is

deployed at depth, prime the filter with molecular-grade water prior to deployment. Use a clean syringe to fill the filter or place the inflow of the sampling pump into the water source and use

the Prime Menu’s “RUN WATER” command.

The SASe is slightly negatively buoyant but it should be attached to a dive weight or to an

underwater structure to prevent it from moving in waves or current. If attached to a solid

structure, the SASe should be tightly secured to prevent wear on the housing. For long

deployments, large stainless-steel hose clamps work better than zip ties which can stretch and

loosen under stress over time.

Once a sample has been collected, the filter or the entire sampling cartridge must be replaced to

continue daily sampling or set new dates and time for single sampling. New filters must have

check valves and be primed with purified water. This filter/cartridge replacement can be done as

many times as the battery life will allow, typically five to six times for 1000mL samples.

Completed samples are returned to the lab for analysis. The preservative acts to preserve the

DNA samples for weeks to months at room temperature [1, 2]. The check valves on the filter

have a 2.9 psi cracking pressure to prevent sample contamination, loss, or dilution; however, the

filters should be further sealed with luer lock caps after collection to ensure no sample is lost due

to rough handling while awaiting laboratory analysis.

### 6.9. Downloading sample data

To retrieve sampling data, remove the internal armature from the housing and remove the

microSD from the circuit housing. Download the two text files, sampleParam.txt and

dataLog.txt. The sampleParam file retains the settings and sampling parameters as described earlier. The dataLog file has a line of text for every sample taken which includes the sampling

start time and battery voltage.

Example: 9:30:1,18/11/2019,10.74

Key: Hr:Min:Sec (Sampling started),Day/Month/Year (Sampling started),Voltage (volts)

The programming for the SASe requires these two text files to operate; do not remove the files

from the microSD card when downloading the data and reinstall the card before storing or

redeploying the SASe.

### 6.9. Cleaning

The SASe should be rinsed and cleaned with freshwater to remove any sediment, growth, and/or

salt. The tubing for the sample and preservative pumps should be rinsed with molecular-grade

water using the Prime Menu’s “RUN WATER” and “RUN SYR.” command. Press enter on

either command to start its associated pump and press enter again to turn it off. To remove any

biological material from the SASe sampling system, the pump tubing should first be flushed with

freshwater and then soaked in a 5% bleach solution. To soak the sampling system, connect one

piece of tubing to the inflow fitting and another piece of tubing to the syringe connection. Place

the free ends of both tubes in a container of 5% bleach solution. Use the Prime Menu to run the

bleach water through the tubing for both the sample pump and the preservative pump. Once the

SASe tubing and the fittings are completely filled allow the bleach solution to sit for 30 minutes

and then flush the tubing thoroughly with molecular-grade water to prepare the SASe for the

next deployment.

### 6.10. Storage

After cleaning the SASe, it can be stored until future use. To extend the battery life, the power

connection can be disconnected from the circuit board. While it is possible to have multiple

deployments of the SASe off the same battery pack, it is recommended that fresh batteries are

replaced whenever possible to limit the chance of partially processed samples, resulting from low

or dying battery power. Once the coin cell battery voltage drops below 3 volts, it will no longer

power the RTC. To avoid sample timing errors, the time on the SASe should always be checked

and reset, if necessary, before deployment.

References:

[1] DNAgard® Tissues & Cells Handbook. Item No. 9101. Rev. 08/2011. [Online]. Available:

https://www.biomatrica.com/download/hp-dnagard-tissue-

handbook/?ind=1519868897797&filename=9101-

0811.pdf&wpdmdl=580&refresh=5efb407ad50a71593524346 (Accessed 10.15.20)

[2] DNA/RNA Shield Zymo Research product description. [Online]. Available:

https://files.zymoresearch.com/protocols/_r1100-50_r1100-250_r1200-25_r1100-

125_dna_rna_shield.pdf (Accessed 5.27.21)

Figures & Tables:

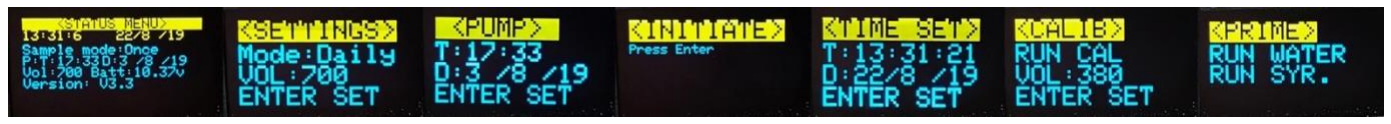
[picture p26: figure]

Figure 1: The seven menus in the SASe user interface with the menu title in highlighted in

yellow at the top. Left to right: Status Menu, Settings Menu, Pump Menu, Initiate Menu, Time

Menu, Calib Menu, Prime Menu.

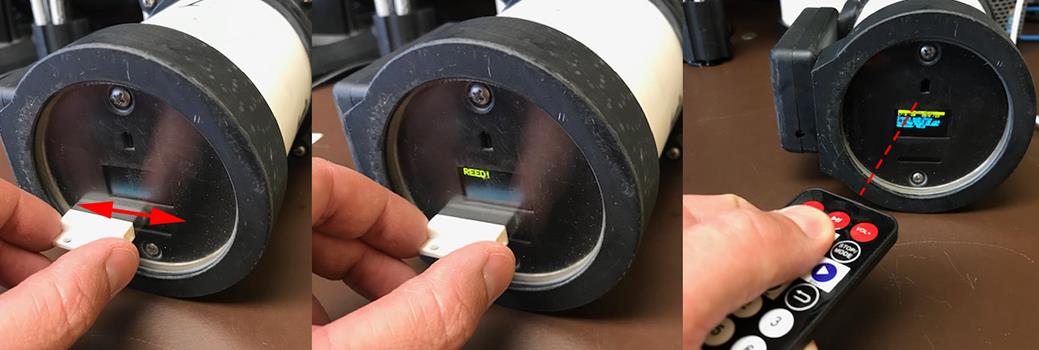
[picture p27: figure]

Figure 2: Moving a magnet across the face of the reed switch will wake the SASe from sleep

mode. With line of sight, the IR remote can be used to communicate with the IR receiver for

navigating through the SASe menus.

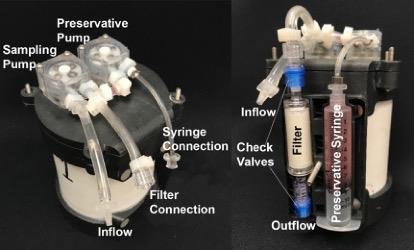
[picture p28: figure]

Figure 3: The external components of the SASe sampling system labeled for reference.

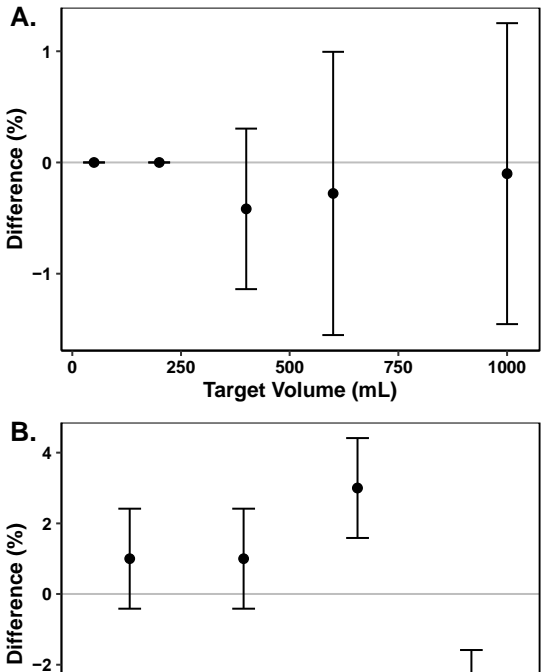
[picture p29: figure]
Target Volume (mL); Difference (%) A.; Difference (%) B.
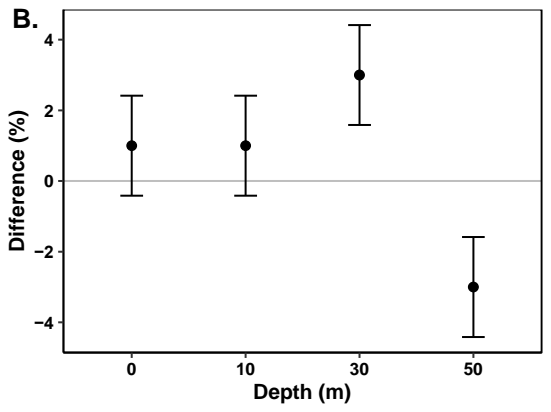
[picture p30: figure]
Depth (m)

Figure 4: Percent difference in the volume of water programmed to be filtered vs that collected

as a function of (A) targeted volume and (B) depth. Error bars are standard deviations.

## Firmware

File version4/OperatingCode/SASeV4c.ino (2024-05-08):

#include <Adafruit_NeoPixel.h>

//Libraries needed are:
// 1. Adafruit SSD1306, in Teensy folder if Teensy has been installed on computer. Note: the h file needs to be commented and uncommented to select the correct oled screen resolution 128 x 64
// 2. Adafruit GFX Library (in local documents folder)
// 3. SdFat (in local documents folder)
// Update note: Due to changes to ADC.h library the code must be ammended for multiple instances in the Setup. Where: adc->setAveraging(32, ADC_0) change to: adc->adc0->setAveraging(32) (and make similar changes to next two instances), also adc-> becomes adc->adc0->.
// Changed syringe volume to 7mL to accomodate disparity in pump rates. With new tubing should be reset to 6mL
// Changed Run Water and Run Syringe commands in Prime menu to turn on and off with enter button rather than limiting to 10 sec
// Encoder values made absolute on lines 566 & 574 to avoid issue with motors not stopping (e.g. syringe pump running forever)
char saseVersion [] = "V3d"; //V3d Updated code for use on Teensy 4.1, comments below

//LIBRARIES/Users/fas/Desktop/AOML/SASe/code_/libraries_/Encoder.h
  #include <TimeLib.h>//Time library
  #include <Wire.h>// I2C library
  #include <Snooze.h>// Low power sleep library for Teensy, Needed to edit two files related to snooze, SnoozeDigital.cpp and hal.c, follow guidance on https://github.com/duff2013/Snooze/issues/108 and https://github.com/duff2013/Snooze/issues/114 to fix
  //Previously we've used Hibernate function from the snooze library for sub mA current draw in sleep mode. With the new Teensy 4s and a unmaintained library it isn't working anymore. Sleep function does work.
  //It's not as low current draw but it will still allow for short-term deployments (maybe days, need to check current draw)
  #include <Adafruit_GFX.h>// OLED graphics library
  #include <Adafruit_SSD1306.h>// OLED library
  #include <IRremote.h>// Needed to enable line 51 in IRremote.hpp (#define SUPPRESS_ERROR_MESSAGE_FOR_BEGIN, files on my mac in /Users/.../Library/Arduino15/packages/teensy/hardware/avr/1.58.1/libraries/IRremote/src), also needed to change some variables, mainly "irrecv" to "IRreceiver" (see for guidance: https://github.com/Arduino-IRremote/Arduino-IRremote?tab=readme-ov-file#converting-your-2x-program-to-the-4x-version)
  //Uncomment line 174 and open serial monitor while pressing remote buttons to see what codes each IR button is generating. Need to make sure code IDs are used in IR definitions
  #include <SdFat.h>//sd cart library needed to make some updates to variables, but all done in code here
  #include <SD.h>//sd library
  #include <SPI.h>// Serial library
  #include <ADC.h>// Analog to digital converter library
  #include <ADC_util.h> //Added in following ADC examples
  #include <Encoder.h>
//DEFINITIONS
  //Snooze
    SnoozeAlarm alarm;
    SnoozeDigital digital;
    SnoozeBlock config_teensy40(digital, alarm);
    int hrToSleep;// Number of hours to sleep
    int minToSleep;// Number of remaining minutes to sleep
    int secToSleep;// Number of remaining seconds to sleep
  //OLED
    #define OLED_RESET 8// OLED reset
    Adafruit_SSD1306 display(OLED_RESET);
    int oledPowerPin = 17;// Pin that powers the OLED
  //Voltage Read
    int voltageReadPin = A2;// Pin that reads the voltage
    ADC *adc = new ADC();// Creates adc object
    float voltage = 0;// The voltage of the battery backs
    float rawVoltage = 0;// The raw voltage read across the voltage divider
  //IR
    int irPowerPin = 20;// Pin that powers the IR sensor
    #define IR_RECEIVE_PIN 21
    //Original code
    // #define LEFTIR 16584943// IR signal read by sensor that translates to LEFTIR
    // #define RIGHTIR 16601263// IR signal read by sensor that translates to RIGHTIR
    // #define UPIR 16621663// IR signal read by sensor that translates to UPIR
    // #define DOWNIR 16625743// IR signal read by sensor that translates to DOWNIR
    // #define ENTERIR 16617583// IR signal read by sensor that translates to ENTERIR
    //NEED TO UPDATE THE IR HEX NUMBERS (BELOW) TO PROPERLY BE READ BY REMOTE. Uncomment line 172 for further troubleshooting in serial monitor
    //Normal Remote Below
     #define LEFTIR 0xF708BF00      // IR signal read by sensor that translates to LEFTIR
     #define RIGHTIR 0xF50ABF00     // IR signal read by sensor that translates to RIGHTIR
     #define UPIR 0xFA05BF00        // IR signal read by sensor that translates to UPIR
     #define DOWNIR 0xF20DBF00      // IR signal read by sensor that translates to DOWNIR
     #define ENTERIR 0xF609BF00     // IR signal read by sensor that translates to ENTERIR 
    //Convenient Remote Below
   // #define LEFTIR 3910598400// IR signal read by sensor that translates to LEFTIR
   // #define RIGHTIR 4061003520// IR signal read by sensor that translates to RIGHTIR
   // #define UPIR 3927310080// IR signal read by sensor that translates to UPIR
   // #define DOWNIR 3877175040// IR signal read by sensor that translates to DOWNIR
   // #define ENTERIR 3860463360// IR signal read by sensor that translates to ENTERIR
  //Reed switch
    int REED_INTERRUPT_PIN = 22;// Pin that reed switch is attached to
  //Pumps
    float maxBattVoltage = 10.50;// Max battery voltage, at which the calibration is run
    int pumpAPin =38;// Pin to signal FET to drive motor 1
    int pumpAEncPowerPin = 36;
    int pumpAEncAPin = 37;
    int pumpAEncBPin = 35;        
    Encoder pumpAEnc(pumpAEncAPin, pumpAEncBPin);
    long pumpAGearRatio = 34.0;
    long pumpAVolume = 0.0;

    int syringePin =27;// Pin to signal FET to drive motor 2
    int syringeEncPowerPin = 29;
    int syringeEncAPin = 28;
    int syringeEncBPin = 30;  
    Encoder syringeEnc(syringeEncAPin, syringeEncBPin);
    long syringeGearRatio = 99.0;
    long syringeVolume = 0.0;

    long sampleVolumeChangeMl = 10.0; //Units of change for sampling volume 
    long calibrationVolumeChangeMl = 1.0; //Units of change for calibration volume
    long calibrationCount = 0.0;
    long calibrationVolume = 1.0;
    int waitforit = 0;

  // Menu
    uint8_t menu = 0;// An index value to establish which navigation menu is currently selected
    uint8_t pos = 0;// An index value to establish which navigation position (within a menu) is currently selected
  //sd card
    #define SD_CONFIG SdioConfig(FIFO_SDIO)
    FsFile sampleParam;// Name of sample parameter file saved on sd card
    FsFile dataLog;// Name of data logging file saved on sd card
    #define SAMPLE_PARAM_ROW 1// Number of rows in sampleParam.txt file
    #define SAMPLE_PARAM_COL 9// Number of columns in sampleParam.txt file
    int sampleParamArray[SAMPLE_PARAM_ROW][SAMPLE_PARAM_COL];// Create an sampleParamArray with SAMPLE_PARAM_ROW rows and SAMPLE_PARAM_COL columns
  
  //RTC
    time_t nowSecTime;// Create a time variable called nowSecTime, representing the time now in seconds since 1970
    time_t updateSecTime;// Create a time variable called updateSecTime, representing the time to be set to the RTC in seconds since 1970
    time_t aSecTime;// Create a time variable called aSecTime, representing the time to fire pump A in seconds since 1970
    time_t bSecTime;// Create a time variable called bSecTime, representing the time to fire pump B in seconds since 1970
    int nowHr; int nowMin; int nowSec; int nowDay; int nowMon;  int nowYr;// create integers for the time now in hours, minutes, seconds, days, months, years
    int aHr;int aMin;int aSec;int aDay;int aMon;int aYr;// create integers for the time to fire A in hours, minutes, seconds, days, months, years
    long aEndTime;
    int aAlarmFlag = 0;
  //Sample Parameters. For sampleMode 0 is daily, 1 is once
    int sampleMode;// An integer to hold what sampling mode is initiated, 0 for daily, 1 for once
    long sampleVolume = 5.0;// An integer for the number of mL of sample that will be collected
    long syringeDispenseVolume = 7.0; //Volume of preservative pumped from syringe

//<-------------------------------------------------------------------------------------------------------------------------------------------------------------->
//<----------------------------------------------------------------------SETUP----------------------------------------------------------------------------------->
//<-------------------------------------------------------------------------------------------------------------------------------------------------------------->
void setup(){// Run setup code on initial power up
  //Communication setup     
    //Wire.begin();// NOT SURE THIS IS NECESSARY
    Serial.begin(9600);// Initiate the serial connection, used for debugging
    delay (500);// Pause for a half second
  //Voltage read setup
    pinMode(voltageReadPin, INPUT);// Set the voltage read pin as an input, where we will be reading the voltage of the battery pack
    adc->adc0->setAveraging(32); // set number of averages read in the analog to digital converter we will use to read the voltage of the battery pack
    adc->adc0->setResolution(16); // set bits of resolution of the analaog to digital converter we will use to read the voltage of the battery pack
    adc->adc0->setConversionSpeed(ADC_CONVERSION_SPEED::VERY_LOW_SPEED); // change the conversion speed, added this command in to follow example guidance
    adc->adc0->setSamplingSpeed(ADC_SAMPLING_SPEED::LOW_SPEED); // set the sampling speed of the analaog to digital converter to low
  //RTC setup          
    setSyncProvider(getTeensy3Time);// Sets the time using the getTeensy3Time function
  //Snooze
    pinMode(REED_INTERRUPT_PIN, INPUT_PULLUP);
    delay(200);
    digital.pinMode(REED_INTERRUPT_PIN, INPUT_PULLUP, RISING);// Sets the pin the reed switch is connected to as an interrupt pin that can wake the teensy up from sleep
    alarm.setRtcTimer(0, 1, 0);// Set the alarm to go off at hour, min, sec

  //OLED Setup
    pinMode(oledPowerPin, OUTPUT);// Set the oledPowerPin to an output because this is the pin that we power the OLED from
    digitalWrite(oledPowerPin, HIGH);// Set the oledPowerPin to high to turn on the OLED
    display.begin(SSD1306_SWITCHCAPVCC, 0x3C);// Begin and initialize the OLED display
    display.clearDisplay();// Clear the OLED display
  //Infrared Setup
    pinMode(irPowerPin, OUTPUT);// Set the irPowerPin to an output because this is the pin that we power the IR sensor from
    digitalWrite(irPowerPin, HIGH);// Set the irPowerPin to high to turn on the IR sensor   
    IrReceiver.begin(IR_RECEIVE_PIN, DISABLE_LED_FEEDBACK);// Starts the IR receiving object irrecv
  //Pump Setup
    pinMode(pumpAPin, OUTPUT);// Set the pumpAPin to an output because this is the pin that we will use to power pump A
    pinMode(pumpAEncPowerPin, OUTPUT);
    pinMode(syringePin, OUTPUT);// Set the syringePin to an output because this is the pin that we will use to power the syringe pump
    pinMode(syringeEncPowerPin, OUTPUT);  
    pumpAEnc.write(0);
    syringeEnc.write(0);
    
  //sd Setup
    bool ok;
    ok = SD.sdfs.begin(SdioConfig(FIFO_SDIO));
    if (!ok) { display.setTextColor(WHITE,BLACK);  display.setTextSize(1);  display.setCursor(2,8);  display.println("Microsd not");display.setCursor(5,16);  display.println("detected!");display.display();}// If the sd card fails to communicate, display that the card is not detected to the serial debugging
    readSampleParamArray();// Call the function that reads the sample parameters off of the sd card
    Serial.println(sampleVolume);
    calculateInitialAlarmSecondTime();    
}
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
